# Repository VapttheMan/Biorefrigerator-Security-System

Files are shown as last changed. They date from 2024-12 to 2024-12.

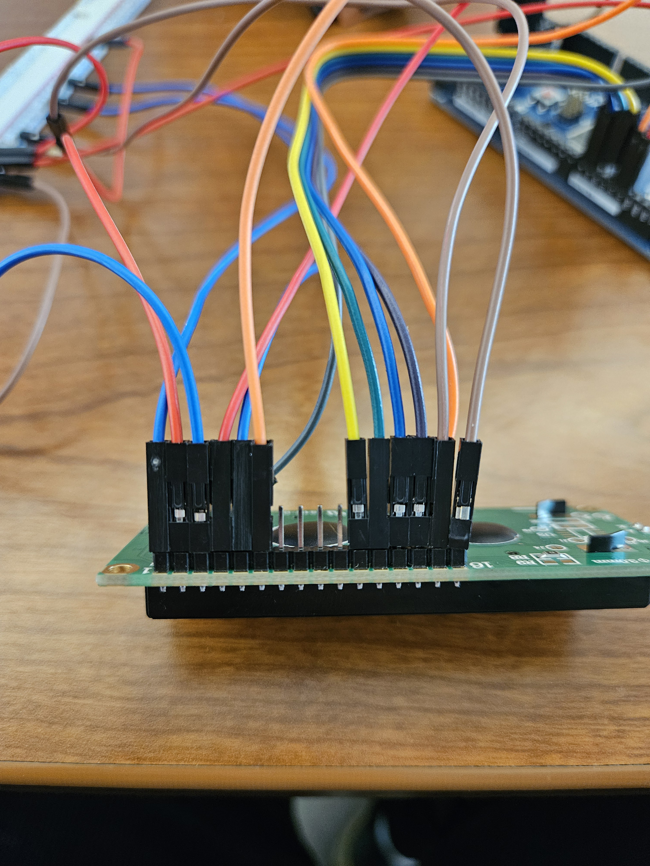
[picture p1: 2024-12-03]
1. Progress Reports/PR4/Photos/20240516_150257.jpg

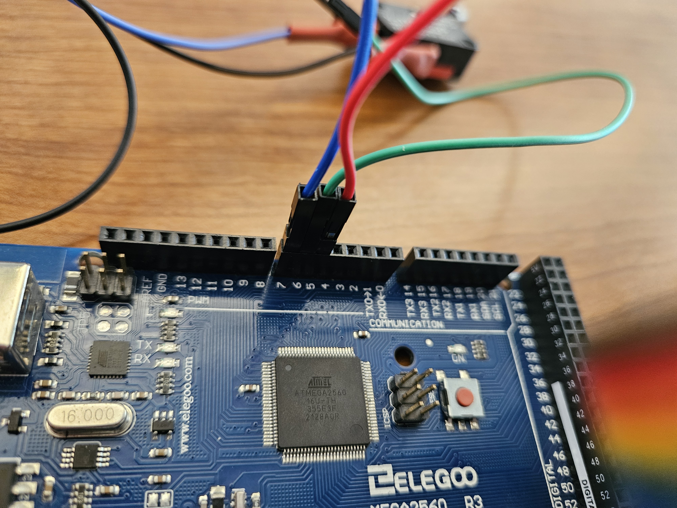
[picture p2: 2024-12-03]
1. Progress Reports/PR4/Photos/20240516_135011.jpg

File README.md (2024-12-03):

# Biorefrigerator Security System

**Contributors:**
- Brayden Chipman
- Vance Padilla
- Ashwin Halepet
- Miguel Cruz

**Note:** This project was initially uploaded to GitHub for visibility and sharing with potential employers and hiring professionals on platforms like LinkedIn. It was originally stored on Google Drive.

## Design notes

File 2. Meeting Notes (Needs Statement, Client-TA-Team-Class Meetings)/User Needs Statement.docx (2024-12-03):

Needs Statement:

Version 1:

A way to securely lock the fridges in lab settings to ensure people’s research samples are protected and consistently in the correct environment and something that is adaptable to multiple different types of refrigerators.

Directly from problem statement from client

Version 2:
There is a need for a lock for clinical refrigerators to prevent them from staying open due to the loss of samples

Version 3:

There is a need for a device to prevent clinical refrigerators from opening due to human error in order to prevent the loss of samples through thawing.

Too specific/Solution Oriented

Version 4:

There is a need to reduce the risk of contents in a controlled environment from being compromised due to unexpected/unwanted/unintentional access.

-Removes the focus on specifically refrigerators

Signs

Miguel Cruz (11/15/23, 7:55 PM)

Brayden Chipman (11/15/23, 7:55PM)

Vance Padilla (11/15/23, 7:55PM)

Ashwin Halepet (11/15/23, 7:55PM)

Version 5:

There is a need to reduce the risk of contents in a controlled environment from being compromised due to unexpected, unwanted, or unintentional access in frequently accessed refrigerators.

MC 11:13AM 11/28/23

BC 11:13AM 11/28/23

AH 11:14AM 11/28/23

VP: 11:14AM 11/28/23

Solution Statement:

There is a need to reduce the risk of contents in a controlled environment from being compromised due to unexpected, unwanted, or unintentional access in frequently accessed refrigerators by retrofitting features from more advanced and expensive products into older units. to prevent more major losses in costs.

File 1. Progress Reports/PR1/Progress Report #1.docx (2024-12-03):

Digital Lock for Clinical Refrigerators

Biomedical Engineering Senior Design

Dr. Aijun Wang

Progress Report 1

Fall 2023

Team 1

Miguel Cruz-11:08 am, 10/29/2023

Brayden Chipman-12:13 pm, 10/29/2023

Ashwin Halepet-12:38 pm, 10/30/2023

Vance Padilla - 3:38pm, 10/29/2023

Table of Contents

Problem Formulation 2

A. Background 2

B. Design Problem Statement 3

C. Objective 3

Needs Assessment 4

A. Survey Results 4

B. Needs Flow Chart 5

State-of-the Art 7

A. Introduction 7

B. Patent and Literature Search Results 7

C. Benchmarking Table 12

Preliminary Engineering Design Specifications and Constraints 15

A. EDS Table 15

B. House of Quality 16

References 18

Appendix 19

User Needs Survey R1 19

Additional Patents Chart 22

Client Interview 22

Meeting Minutes 24

Gantt Chart 25

# Problem Formulation

## A. Background

In preclinical and clinical laboratories, refrigerators and freezers are necessary tools for the preservation of samples such as biopsies, antibodies, and enzymes for use in testing and research. In certain situations, these samples can be irreplaceable. Unintentional thawing of these samples may render them unusable for the lab, leading to large losses in both time and money.

Refrigerators have gaskets, which are straps that are on the internal edge of the refrigerator door that seal the refrigerator shut. Inside a gasket is a magnet that uses attraction to shut itself to the metal of the refrigerator in order to seal shut [4]. Additionally, a refrigerator has hinges in order to close properly as well as open and close in a specific direction [6].

Refrigerators can fail to close for a variety of reasons, regardless of whether the refrigerator is in a laboratory environment or not. For instance, refrigerators could potentially lose the sealing capabilities of the gasket (the sealing that helps close the refrigerator door) due the gasket being dirty and old [5]. This can reduce the refrigerator’s capabilities of keeping shut. Another reason why the refrigerator might not be closing is because there are too many items inside the refrigerator and the items could prop the refrigerator door open in order to fit in. In environments where the internal temperature of the refrigerator or freezer is below freezing, ice buildup can also prevent the doors from properly closing. Furthermore, the refrigerator's magnets that can attract the metal of the refrigerator could potentially not function as well as usual, which results in the door potentially not closing properly [3]. Additionally, the refrigerator hinges can be damaged, which can prevent the refrigerator door from closing since the door cannot move properly if the hinges fail to operate properly [6]. Finally, another reason why a refrigerator door will not close is due to human negligence where a person did not shut it tightly enough or did not close it all the way [2].

To prevent this, many refrigerators have displays to show the internal temperature or alarms that go off when the temperature gets too low. Despite this, however, lab refrigerators still get left open often. A reason for this is likely because by time the displays show the low temperature, people are either gone or not paying attention and the samples are compromised. Additionally, alarms may not go off until after hours or may fail. If the equipment is old, it also may not have these features. If the refrigerators still work, a lock would be a cheaper and easier upgrade than installing alarms or displays.

Laboratories are environments in which the potential for human error can be very high. Laboratory refrigerators hold samples and materials that can potentially be worth hundreds of thousands of dollars in materials and research time. Based on client testimonials, laboratory refrigerators have been unintentionally left open, leading to large monetary losses.

## B. Design Problem Statement

Current locking systems for laboratory refrigerators and freezers fail to provide sufficient barriers to human error that would prevent the doors from being left ajar accidentally. Simple mechanical locks may ensure that the doors stay shut, but they lack network integration that would allow for users to verify that the door is shut properly or who has opened the refrigerator recently. The only current solution we have found that solves both issues is sold at a price that is not feasible for many labs, as most labs would have to buy multiple to ensure the integrity of their entire inventory[1]. This solution is the Beol Smart Lock as shown in the Benchmarking Table section. At $984 USD this lock is not feasible to order for the majority of labs. There are other digital locks on the open market that a consumer can buy. Such as on Amazon, where some locks can connect to personal devices and track worker’s usage of the locks (to better figure out who may have accidentally left the door open). However, none of these locks can be used on refrigerators without compromising the structure of the door. A digital refrigerator lock would have to exist solely on the exterior of the refrigerator system.

For these reasons, we aim to create an affordable digital device to increase security with refrigerated products by holding lab members accountable for ensuring the refrigerator door is shut.

## C. Objective

The objective of this senior design project is to develop a digital locking system for laboratory refrigerators and freezers that seamlessly interfaces with a dedicated digital application. We will provide a comprehensive solution that enhances the security and accountability of laboratory refrigerators. By addressing these major requirements and design inputs, the project aims to develop a digital locking system that is accessible, user-friendly, and cost-effective for a diverse range of laboratories.

Needs Assessment

## A. Survey Results

There is a disclaimer for the survey that was conducted by our team that responses from either us or the teaching assistant will be weighted as less than any other responses. Additionally, there are elements of the survey that we conducted that will be improved upon in future renditions of the survey in order to improve user feedback for the project’s user needs. We will make the survey more broadly to serve the needs of various customers since owning lab refrigerators is a very broad category of different users rather than needs based on only our client. We will base our survey more on the general needs of the users potentially impacted by digital locks in refrigerators rather than what aspects the customers desire for the end product. Furthermore, we plan on adding more text to the front of the survey in order to make it clearer on what the survey will accomplish.

The survey respondents of this survey vary from professors to teaching assistants to students. Besides ourselves and our teaching assistants, any other responder will be held in equal weight. However, due to some changes in how we will make our survey, any new responses will hold more weight than before since the new survey will be more polished and it will address problems with our survey. The current survey questions were planned to gauge user interest of needs and possible elements for the design; however, the new survey will go over more user needs. The questions that will be held in the most weight are the free response questions since a person can clarify and respond to their reasoning on why they weigh certain problems or needs more than others and it will help us gauge what is most important and what is the extent of the problems and needs users are facing. Our current survey based user needs off whether a user need is very important, useful but not important, and not important, which are defined as: very important means the user need is absolutely necessary for the design or else the design will not be as beneficial to users, useful but not important means the need is more nice to have but is not required, and not important means that the need is not essential to the final design.

Based on the survey results, the majority of the users do not have any form of locks or securing mechanism to secure their lab refrigerators. A slight majority of users have had their refrigerators open at least once throughout their time in a laboratory environment. Some users indicate a lack of worry with their refrigerators as they have not had issues with refrigerators opening. However, other users have had problems with their refrigerator security either through older parts of the refrigerator or due to unreliable alarm and lock systems. The survey responders universally indicated that they desire a lower priced product in order to save money as well as a smaller product anywhere up to a maximum size of a foot.

## B. Needs Flow Chart

The most important requirement is to safeguard the integrity of valuable laboratory samples. The digital lock system will provide a remote locking and unlocking mechanism for refrigerator doors, directly addressing the critical user need to prevent unintentional spoilage of samples due to doors being left ajar. A primary design input is the creation of a system capable of reliably protecting these valuable, often irreplaceable, samples.

Another core consideration is the prioritization of personnel accountability. This requirement calls for the integration of digital features that enable real-time user logs and remote alerts. By tracking and recording personnel interactions with the locking mechanism, the project aims to enhance accountability within laboratory settings. The design input focuses on creating a digital application that seamlessly syncs with the locking system, facilitating user management and monitoring.

Additionally, cost-effectiveness is a key aspect of the objective. The project aims to design an affordable solution that overcomes the high price barriers associated with existing locking systems. This design input aligns with the overarching need for an economical digital device that improves security and accountability, ensuring accessibility for laboratories of varying sizes. Cost-effectiveness also ties into another direct need from end users, that being the longevity of the product. It is a major benefit to end users to have a product that will not have to be replaced for some time.

In addition to these major requirements, there are other considerations that, while not primary requirements, would be valuable inputs for the design of the locking device. A user-centric approach is something to consider, with the aim of creating a user-friendly interface that simplifies the process of remote locking and unlocking. In the process of making this product more accessible, interacting with the locking system becomes easier. This however, is not a characteristic that would drastically impact the functionality of the product. This approach addresses the need for an intuitive digital application and locking mechanism design, making it easy for laboratory staff to use.

Compatibility and integration are also considerations for the design. The digital lock system should seamlessly fit a wide range of refrigerator models commonly found in laboratories, addressing the diversity of laboratory equipment. The design inputs will focus on ensuring compatibility and integration capabilities.

Security was one of the characteristics that was not a priority for many, given the survey results. Given that the primary clientele of this product is laboratory staff, there was not as much a concern of stealing, rather a concern that the refrigerator doors stay closed. As a result, physical barriers towards theft and physical damage were not of a higher priority.

Below is shown the needs flow charts which summarizes what considerations are essential to not needed.

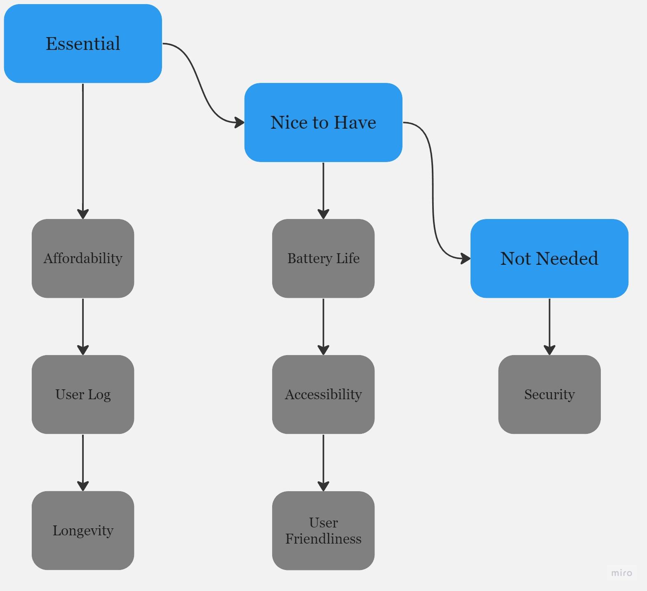
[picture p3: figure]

# State-of-the Art

## A. Introduction

While there have been some similar refrigerator lock products on prior patents, including some with digital unlocking and locking systems, none have had digital locks that connect internet enabled devices. Aside from that, these devices have features that we could draw inspiration from for our digitized refrigerator locks, as well as information on what features are missing from the current market.

## B. Patent and Literature Search Results

I. US20210071940A Patent

i. Cooler and Freezer Lock

ii.William Denison, Calin Roatis

iii. The product is a lock that can be utilized to open and close a freezer. Access is controlled with controllers that can unlock and lock the refrigerator door. There is a digital component to these locks as each controller is controlled by a microcomputer. Furthermore, there is an electronic system in the device in order to help perform the unlocking and locking actions. A drawback of this system is that the lock is a complicated design that can confuse users. This product can serve as inspiration for our potential device since the digital lock will be an electronic system and we can base our product on this in order to gain inspiration on how to create an electronic designed digital lock.

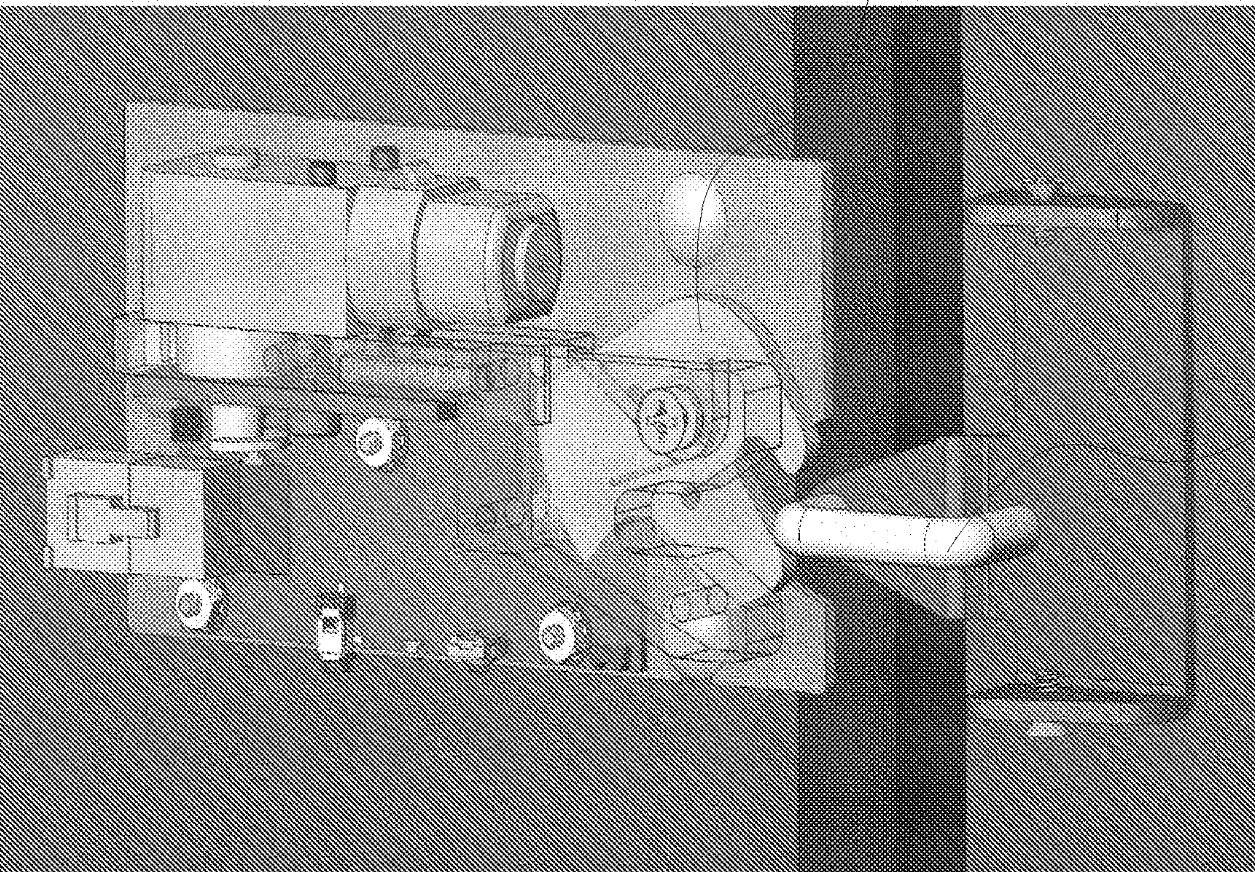
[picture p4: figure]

II. US7768378B2 Patent

i. Field retrofittable refrigerator lock with audit trail

ii. Brian R. Hill, Steven A. Belzek, Robert Brewcyznski, Kenneth A. Kaczmarz, Mitchell S. Mlynarczyk, Francis H. Zimmerman, Ernest Vaughn

iii. The product is a refrigerator lock with a number punch-in code attached on the front of the lock in order to secure the refrigerator with a passcode. The product contains digital components due to the punch in code that resembles a phone. The product can track user information, as well as when the user opened and closed the refrigerator. The main drawback of this product is that the phone system that is used is rather dated and most people use more digital versions of phones in this day and age. However, this product can serve as inspiration since this product uses a phone network, similarly to how a digital lock has a phone like interface within a digital app, in order to ensure the lock is locked.

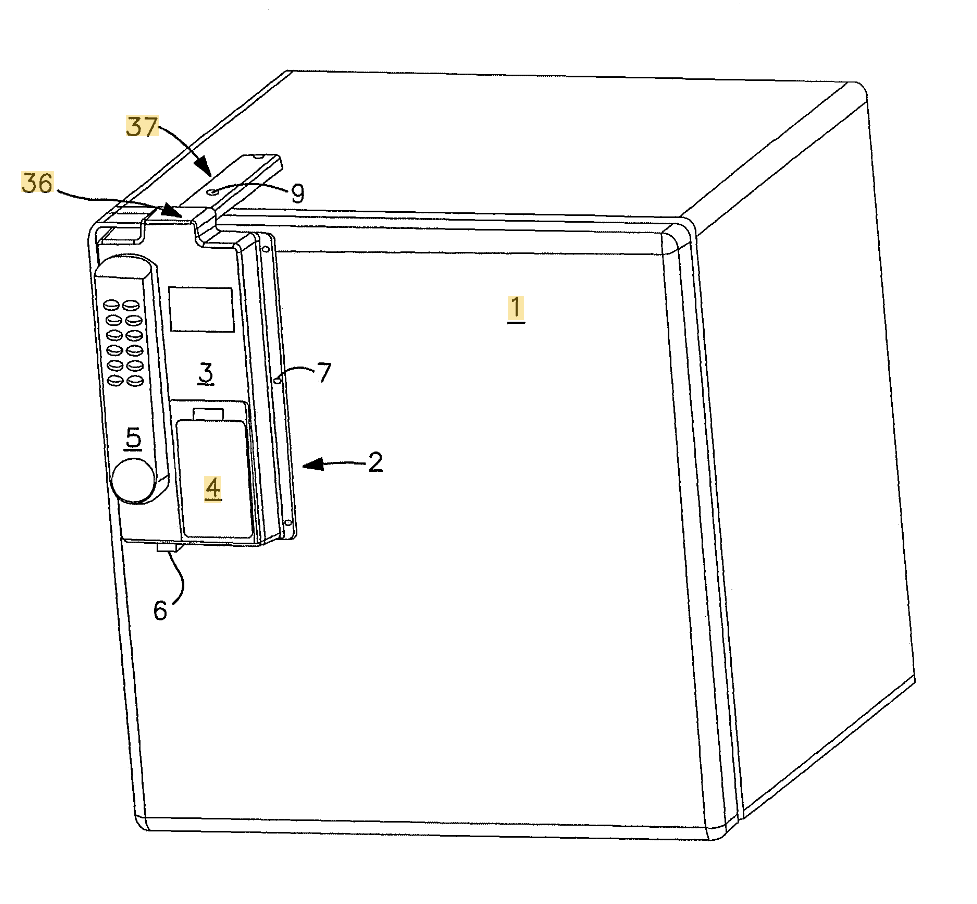
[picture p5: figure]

III. US8063735B2 Patent

i. Remotely actuated refrigerator lock with thermal spoilage protection

ii. Norman A. Shoenfeld

iii. The product is a remote door lock system that can be accessed via a computer. The product can be connected to a computer either by ethernet or by a USB system. The product can track the temperature and humidity within the system so that when the temperature and humidity reaches a threshold, the remote connected unlocking and locking will be disabled in order to regulate temperature and humidity. This product also maintains a log of people who access the refrigerator. The biggest drawback of this design is that it is a rather large device that does take up space. This design is relevant to our brainstorming process since this design is remotely controlled and that it connects to devices via some form of an external network.

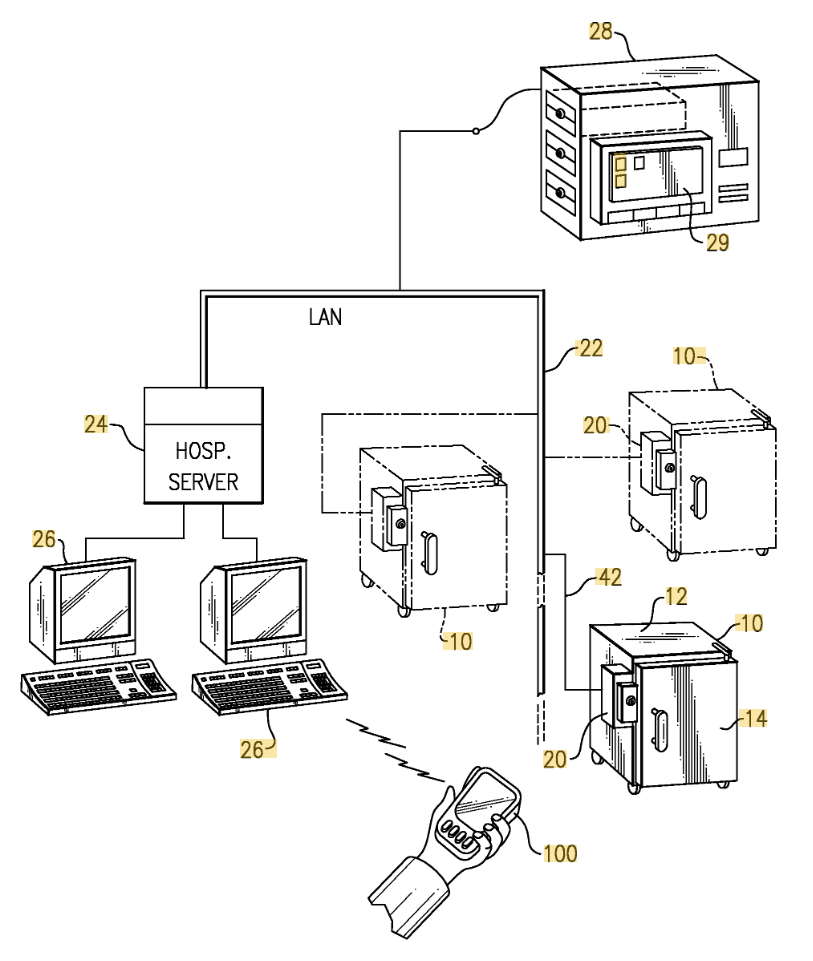
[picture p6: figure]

IV. US20170219271 Patent

i. Refrigerator Locking System

ii. Carl Kent Abrahamson

iii. This product is a lock that can lock multiple doors of the refrigerator at once in just one location of the refrigerator. This is a quite versatile lock since it can close a number of locks at once in the same refrigerator cabinet while not requiring any additional devices or parts. A drawback of this device is that there is not anything digital about this device. This could serve as inspiration for if we decide to expand the product and create a device that can close multiple refrigerator doors at once.

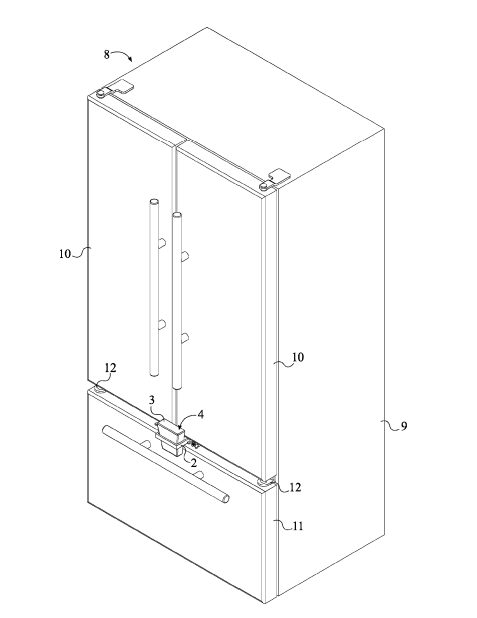
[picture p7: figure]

V. Becton Dickinson Pyxis ES Refrigerator

This device is a refrigerator that stores medications and encodes in the users so that the doctor knows who uses what medicine that is stored in the refrigerator as well as the location. This device requires signing in and signing out in a screen that is on the refrigerator in order to access the medication, hence why this device is a digital lock. Furthermore, this device has a physical key spot so that a person could also access it with a physical key. There are various versions and sizes of this device depending on user needs. A drawback of this device is that the screen has a lot of options and it can get complicated when looking for the basic items since the screen keeps a vast log of medications and users, though it is only a light drawback. This device can serve as inspiration for our future device since it can give us ideas on how a sign in feature can work on our app as well as some ideas on aspects of the app to add.

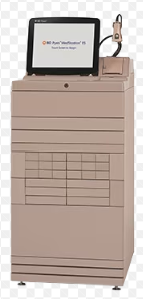
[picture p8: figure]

There have been previous recalls on digital refrigerator unlocking and locking devices used for storing biological and/or medical substances, though they are limited in frequency. There have been prior problems where a user signs in to access the refrigerator and the refrigerator does not open. According to MAUDE, in 2021 and 2022, there has been one recorded incident in both years for the Becton Dickinson Pyxis ES Refrigerator, where the refrigerator refused to unlock due to a malfunction, and as a result, a customer could not get their medications that the doctor prescribes, even though in one of the cases, the patient refused treatments. This is a very serious recall since if a patient needed to get their needed medicine, if the refrigerator refuses to unlock, then the patient could ultimately die since they could not get their medicine. Our digital lock should automatically open when a user chooses the unlock option as well as have a physical override.

## C. Benchmarking Table

Due to the specificity of the problem that this project is meant to address, a benchmarking table was created in order to compare the important metrics of similar products. The benchmarking table is a neat and convenient method to collect ideas on what one can expect in terms of price and other metrics based on similar devices. The user needs that were chosen were based on survey results as well as team discussions with each other, the Teaching Assistant, and the client. The benchmarking table compares similar products’ solutions to user needs along with their metrics and units. The BEOL Biological Refrigerator Smart Lock was chosen to be benchmarked and compared due to the fact that it is the only current digital locking solution for refrigerators in a laboratory setting that is on the market, even though they only sell in China and the pricing is high. Due to the high feature set and price of the BEOL lock, this lock can be considered very useful yet very niche. The goal of this project is to make a more widely accessible lock while still maintaining much of the specialized functionality that comes with network and remote integration. The reason the Sifely Smart Lock was chosen is because the product is a digital lock used for any lock that connects to a phone app. While not direct competition for the product this project seeks to create, the Sifely Smart Lock sets a general guideline for features and a user interface that users are satisfied with in regards to remote control of the lock and with everyday usage. The YEYA Refrigerator Lock was chosen based on the information that it was one of the best selling refrigerator locks on Amazon, a shopping service that would be widely available to people both in and out of labs. By using this device as one of the products to benchmark, one is able to compare current user needs to a general refrigerator lock without any digital capabilities, similar to a control group in an experiment.

BENCHMARKING TABLE 10-20-23

TEAM 1: Brayden Chipman, Miguel Cruz, Ashwin Halepet, Vance Padilla
Need | Metric | Units | BEOL Biological Refrigerator Smart Lock * | Sifely Smart Lock | YEYA Refrigerator Lock
1 | Cost | US Dollars | $984 | $129.99 | $13.99
2,4,6,7 | Remote Connectivity | Binary | Yes | Yes | No
4,7 | Size | Centimeters | 15.9 cm x 8.8 cm x 3.6 cm | 17.78 cm x 7.62 cm x 2.84 cm | 25.4 cm x 6.60 cm x 2.54 cm
3,7 | Material | Type | PC-ABS engineering plastics | Zinc | Polypropylene Plastic
3,7 | Strength | Young's Modulus of Material(MPa) | 1670-11100 MPa | 96500 MPa | 800-8250 MPa
3,4,6,7 | Method of Attachment | Type | Adhesive | Installation on Door | Adhesive
4,5,7 | Power Delivery | Type | 2 AA Batteries | 4 AA Batteries | N/A
2,6,7 | Method of Verification | Type | NFC Card, physical key, remote authorization | App, Fingerprint, Passcode | Key
7 | Alarms/Notifications | Binary | Yes | Yes | No
4,6 | Weight | Kilogram | ~3 kg | ~1.65 kg | 0.2 kg
4,6 | Used Outside of Labs | Binary | No | Yes | Yes
1 | Affordability | *Translated using DeepL Translation
2 | Records
3 | Longevity
4 | User Friendly
5 | Battery Life
6 | Accessibility
7 | Security

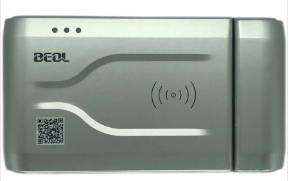
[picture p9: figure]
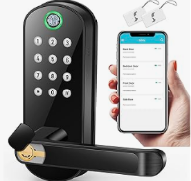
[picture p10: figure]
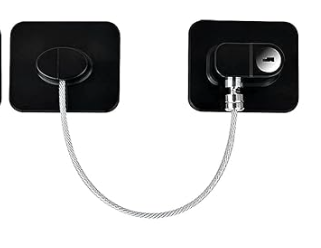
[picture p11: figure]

Images
Description of Products | | | This is a digital lock that was specifically designed for biological refrigerators. It includes a temperature monitor, and features that can close the lock based on changes in temperature. | This is a digital lock that has unlock and lock features connected to a mobile application used to replace the traditional lock and doorknob system. | This is a non-digital lock that is held by a thick wire. The black squares are held up by adhesives that stick to the refrigerator.

# Preliminary Engineering Design Specifications and Constraints

## A. Target Values

This is the current rendition of the preliminary engineering design specifications table. Each of the design metrics was created with one central user need in mind. However, due to the overlapping nature of the needs and properties required to satisfy those needs, most metrics have interplay with each other. One example of this would be the metrics relating to the attachment of the device, as the method of attachment is also directly related to the strength of that attachment.

Given the feedback from the user needs survey, the metrics that were of high importance to the product’s design were size, price, remote connectivity, notifications, method of attachment, strength of attachment, strength of material, user log, and weight. The size and weight of the device were determined through an average of the competition. The device should be small and light enough to be easily installable, yet not to the point where the device loses physical strength. Therefore, by averaging the values of known products that successfully accomplish their task, the product has a starting point in terms of size and weight. Price was a major concern for a large portion of the survey respondents, and the maximum price was determined to be 300 USD. The closest device to the product that this project is meant to create is the BEOL Biological Refrigerator Smart Lock, which is sold at nearly 1000 USD. Obtaining similar functionality at around 300 USD would make this product much more attractive towards consumers with multiple refrigerators that need to be secured. The user log, notifications, and remote connectivity are all metrics that were decided to be nearly essential to the functionality of this project, and were only present on the expensive BEOL lock. By allowing for users to have access to these more modern features, this product is meant to bridge the gap between the very expensive, feature rich locks and the standard physical locks that are commonly used in older or less funded labs.

Metrics | Units | Corresponding User Needs | Range | Target Value | Direction of Improvement
Size | Centimeters | User Friendliness | 2cm-30.48cm | 16.0 cm x 8.0 cm x 4.0 cm | To be minimized to a point
Price | US Dollar | Affordability | $14-$984 | $~300 | To be minimized
Remote Connectivity | Binary | User Friendliness | N/A | Yes | N/A
Notifications | Binary | Accessibility | N/A | Yes | N/A
Method of Attachment | Type | Longevity | Adhesive or Installation | Acrylic Based Adhesive | N/A
Strength of Attachment | N | Durability | 100-200 | 135 | N/A
Strength of Material | GPa | Durability | 0.8 to 96.5 | 69 (6061 Aluminum) | To be maximized
User Log | Binary | Records | N/A | Yes | N/A
Weight | kg | User Friendliness | 1 kg to 4 kg | 2 kg | To be minimized

## B. House of Quality

After creating a benchmarking table to help compare important metrics of similar products and creating an engineering design specifications table (EDS), combining both tables together will create a house of quality. Not only does the house of quality provide many of the details from both the benchmarking table and the EDS table, the house of quality helps us understand the technical aspects within the customers requests and how each metric focused on affects other metrics required for this device. The house of quality also provides relative weight prioritization and customer importance that is judged based on survey responses. Benchmarking and EDS data is mostly displayed on the bottom.

The house of quality helps greatly with correlating between needs and functional requirements. The table shows that the needs of affordability, user friendliness, and security have many strong relationships with the functional requirements. The house of quality also shows that remote connectivity, and material heavily affect the needs that customers want. The table also displays correlations between each functional requirement. Cost and strength of attachment have many correlations to consider when developing the product. Material, cost, and method of attachment will greatly affect the strength of attachment positively while the use of this product outside of labs may correlate with a decrease in cost. Based on the needs shown on the survey, users request many functional requirements to be improved which are all shown on the house of quality. Remote connectivity, power delivery, method of verification, alarms/notifications, and use outside of labs want to be greatly improved while cost of the product wants to be greatly decreased.

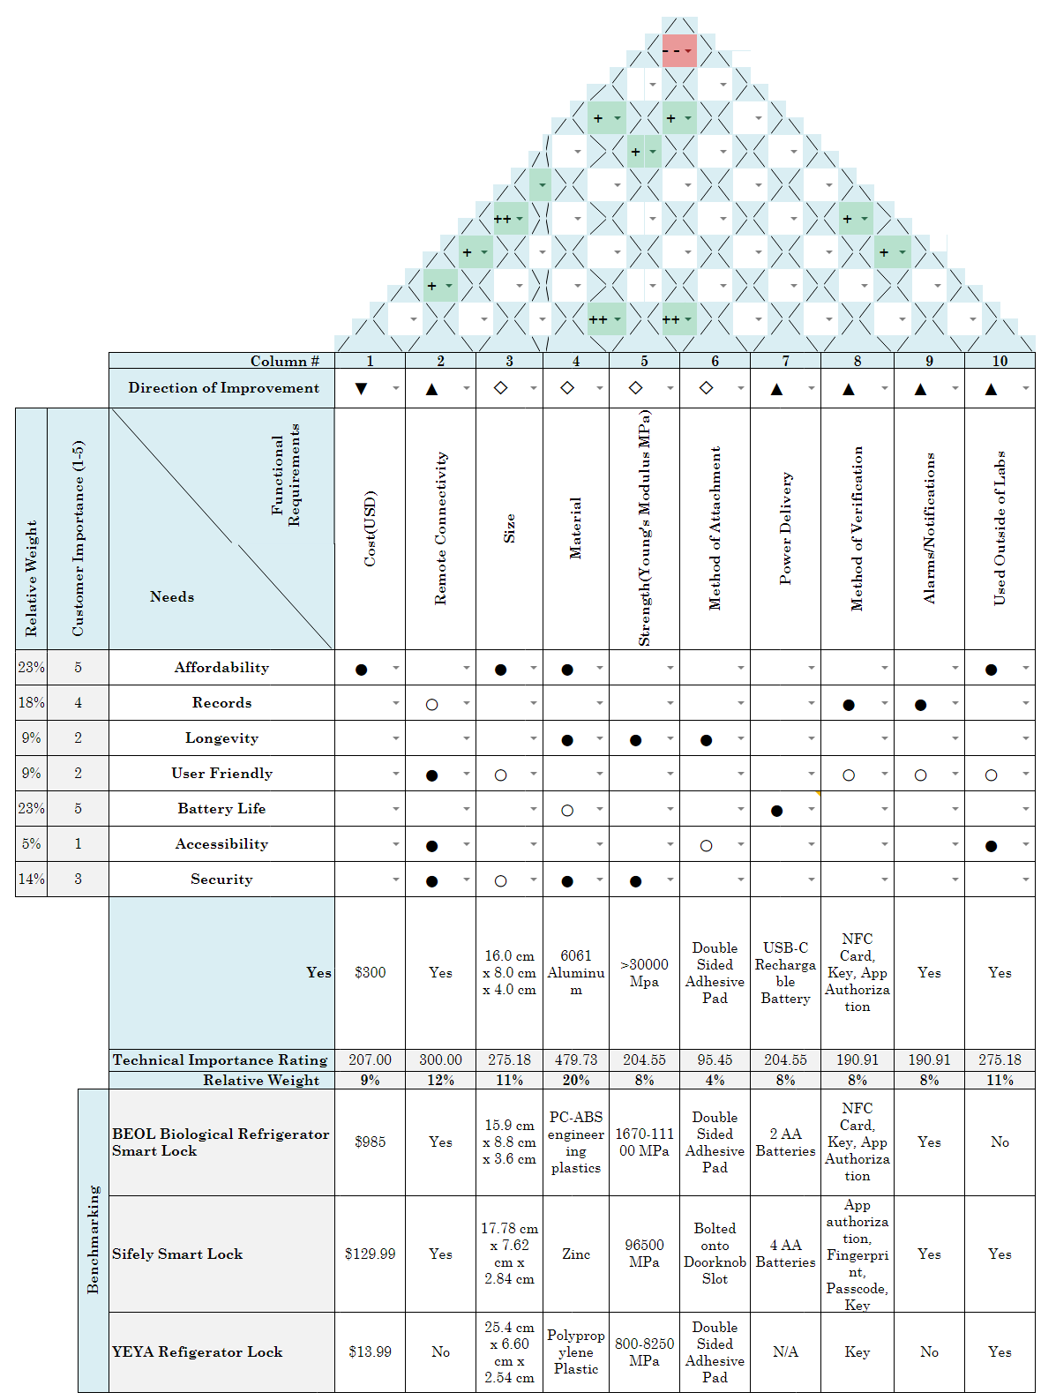
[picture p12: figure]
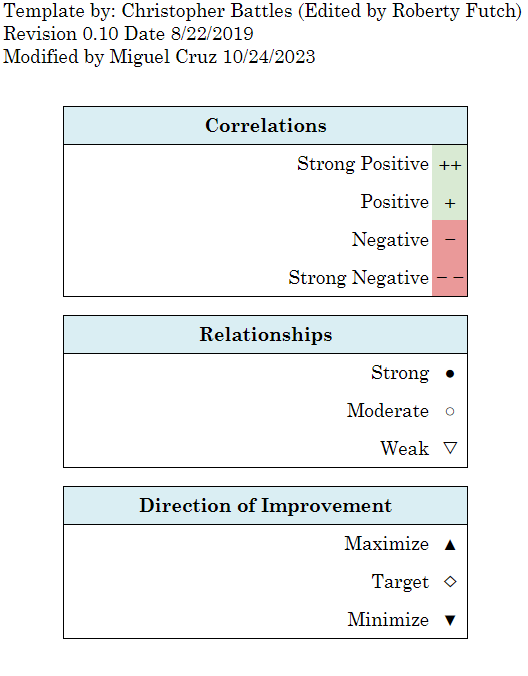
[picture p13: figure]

# References

1. “BEOL贝尔科技生物冰箱智能锁 报警智能冰箱锁 电子锁.” 百度爱采购 - 国内优质的批发采购平台、货源批发网、进货渠道, Qingdao Bell Intelligent Technology Co., Ltd., Accessed 28 Oct. 2023.
2. Appliance, Advanced. “The Fridge Door Won’t Close Properly: Reasons & Solutions.” Advanced Appliance Repair Service, 27 Feb. 2023, Accessed 28 Oct. 2023.
3. “10 Ways to Repair a Refrigerator Door That Won’t Close.” Flamingo Appliance Service, 16 July 2019, Accessed 28 Oct. 2023.
4. Blumberg, Perri Ormont. “Why You Should Clean Your Refrigerator Door Gaskets ASAP.” Southern Living, Dotdash Meredith, 3 Feb. 2020, Accessed 28 Oct. 2023.
5. Crabb, George. “How to Remagnetise a Fridge Door Seal - FIRST4MAGNETS: Blog.” FIRST4MAGNETS, 30 Mar. 2023, Accessed 28 Oct. 2023.
6. Rheuby, Dev. “Selecting the Best Refrigerator Door Hinges: What You Need to Know.” HingeOutlet, HingeOutlet, 6 June 2023, Accessed 28 Oct. 2023.
7. “Maude Adverse Event Report: CAREFUSION 303 Pyxis Es Refrigerator; Automated Dispensing Cabinet.” Accessdata.Fda.Gov, FDA, Accessed 28 Oct. 2023.
8. “Maude Adverse Event Report: Marion Veterans Affairs Medical Pyxis ES Refrigerator; Automated Dispensing Cabinet.” Accessdata.Fda.Gov, FDA, Accessed 28 Oct. 2023.
9. “Overview of Materials for Polypropylene, Molded.” MatWeb, Accessed 28 Oct. 2023.
10. Denison, William, and Calin Roatis. “US20210071940A1 - Cooler and Freezer Lock.” Google Patents, Google, 11 Mar. 2021, Accessed 28 Oct. 2023.
11. Hill, Brian R., et al. “US7768378B2 - Field Retrofittable Refrigerator Lock with Audit Trail.” Google Patents, Google, 3 Aug. 2010, Accessed 28 Oct. 2023.
12. Shoenfeld, Norman A. “US8063735B2 - Remotely Actuated Refrigerator Lock with Thermal Spoilage Protection.” Google Patents, Google, 22 Nov. 2011, Accessed 28 Oct. 2023.
13. Abrahamson, Carl Kent. “Refrigerator Locking System .” Free Patents Online, Anaqua, Inc., 3 Aug. 2017, Accessed 28 Oct. 2023.
14. “Pyxis Medstation ES System .” 50136, Becton Dickinson, June 2013, Accessed 28 Oct. 2023. 50136.com.au/wp-content/uploads/2016/03/Pyxis-Medstation-ES-Station-User-Guide.pdf.

# Appendix

## User Needs Survey R1

Our group utilized Google Forms in order to conduct a survey of various questions. We conducted the survey in order to gain insights on what are the most important user needs to keep in mind during the project. Additionally, we used the survey to understand the extent of the problems with lab refrigerators being left open. Below are the questions that were used in the survey.

Part 1: Introductory Questions

Our group will be conducting a senior design project on creating a digital lock system in order to ensure that refrigerators in the lab are secured. Occasionally in labs, the refrigerator accidentally gets left open, and the consequences can be devastating since open refrigerators can compromise hundreds of thousands of dollars in research. To help prevent this, our group will create a lock that is connected to an app so the lock can secure the refrigerator from being left ajar or slipping open, as well as being able to limit access to selected personnel.

The main information that will be needed for this project are the current issues with locking systems for lab refrigerators and ways that users wish to use the device digitally. We also need other information about possible features that, while not necessary, may be wanted by enough people.

This survey is designed to gather information about needs and wants important to potential end users of our product.

What is your name and email?

Does your lab use locks or any securing mechanism to make sure the refrigerators stay closed?

- Yes
- No

If you answered yes to the previous question, answer the following questions:

Please describe your current system of securing your refrigerator.

What are some issues you have experienced with your current system?

Part 2: User Needs For The Digital Lock

This section is for figuring out the priorities of the end users based on the current locking solutions.

How often have the lab freezers/refrigerators accidentally stayed open throughout your time in the lab?

- 1-2 times
- 3-4 times
- 5 or more times
- Never

Based on your current refrigerator lock solutions, please list the top three design elements that were insufficient in your experience.

Please explain why these features are insufficient.

Please explain your experience with security around your lab.

Part 3: Future Design Elements

This section is about your priorities in looking at possible future design elements for a digital refrigerator lock. Please state your level of priority by selecting one of the three following options: Very Important, Useful But Not Important, and Not Important.

How important is it to be able to monitor the temperature of the refrigerator and have it notify you?

- Very Important
- Useful But Not Important
- Not Important

How important is it to have an app that is associated with the digital lock to record usage of the refrigerator or turn on/off the lock on the refrigerator?

- Very Important
- Useful But Not Important
- Not Important

How important is it that the lock be very difficult to break into?

- Very Important
- Useful But Not Important
- Not Important

How important is the ability for the digital lock to open or close refrigerator doors remotely?

- Very Important
- Useful But Not Important
- Not Important

Based on the previous questions, explain why what you chose is of high priority.

If you would like to explain other priorities that have not been listed, please explain here. Please provide your experience on why this is a priority.

Part 4: Design Input Target Values

When constructing this lock, what are some restrictions that might need to be considered during the design process?

What is the highest price range you would be willing to pay for this product?

- $0-$150
- $150-$300
- $300-$450
- Greater than $450

What are the maximum dimensions for the lock system (full height, width, and depth)?

Are there any other specific details and restraints that one should consider when constructing this refrigerator lock?

Part 5: Free Response

Please give any final statements that you believe must be considered when creating a refrigerator lock. All concerns or ideas will be considered for this project.

Write down any other questions, concerns, or any other essential ideas that have not been listed that you have about this digital lock app project.

## Additional Patents Chart

Patent Number | Title | Inventor | Current Assignee | Source
US20210071940A | Cooler and Freezer Lock | William Denison, Calin Roatis | Individual | https://patents.google.com/patent/US20210071940A1/en?oq=US20210071940A
US7768378B2 | Field Retrofittable Refrigerator Lock with Audit Trail | Brian R. Hill, Steven A. Belzek, Robert Brewczynski, Kenneth A. Kaczmarz, Mitchell S. Mlynarczyk, Francis H. Zimmerman, Ernest Vaughn | CompX International Inc | https://patents.google.com/patent/US7768378B2/en?oq=US7768378B2US7768378B2
US8063735B2 | Remotely Actuated Refrigerator Lock with Thermal Spoilage Protection | Norman A. Shoenfeld | S&S X Ray Products Inc, SIS X Ray Products Inc | https://patents.google.com/patent/US8063735B2/en?oq=US8063735B2
US20170219271 | Refrigerator Locking System | Carl Kent Abrahamson | Individual | https://patents.google.com/patent/US20170219271A1/en?oq=US20170219271

## Client Interview

We met with our client twice. The first meeting was utilized to understand the scope of the project. We discussed the user needs of our client, we learned more on what the current problem is with refrigerator security, which was that refrigerators get left open either on their own or by accident and that can result in loss of years of research and money. We explored the laboratory our client worked in to gain a sense of the environment our client works in. We asked some clarifying questions on potential user needs and priorities. Additionally, we gained some input on survey questions to ask on our surveys. In our second visit, we looked at the Sifely Smart Door Lock to gain some inspiration on potential ideas on what our potential device could look like and also explore how smart locks work.

## Meeting Minutes

Task | 10/8-10/14 | 10/15-10/21 | 10/22-10/28 | 10/29-11/4
Team Meeting | 2 hour | 1 hr | 1 Hr
Client Meeting | 1 Hour | 1 hour
Weekly Deliverables | User Needs Survey | Benchmarking Table | EDS
Miguel Cruz | 50 min | 1.5 hr | 1 hr
Brayden Chipman | 1 Hr 20 min | 1 Hr | 1 hr
Vance Padilla | 1 Hr | 1 Hr | 1 hr
Ashwin Halepet | 1 Hr
Research
Miguel Cruz
Brayden Chipman
Vance Padilla
Ashwin Halepet
TA Meeting | 1.5 hr | 30 min | 1 hr
Project Progress Report
Miguel Cruz | | 2 hr | 3.5 hr
Brayden Chipman | | 2 hr | 4 hr
Vance Padilla | | 1.5 hr | 3 hr
Ashwin Halepet | | 1.5 hr | 2.5 hr

## Gantt Chart

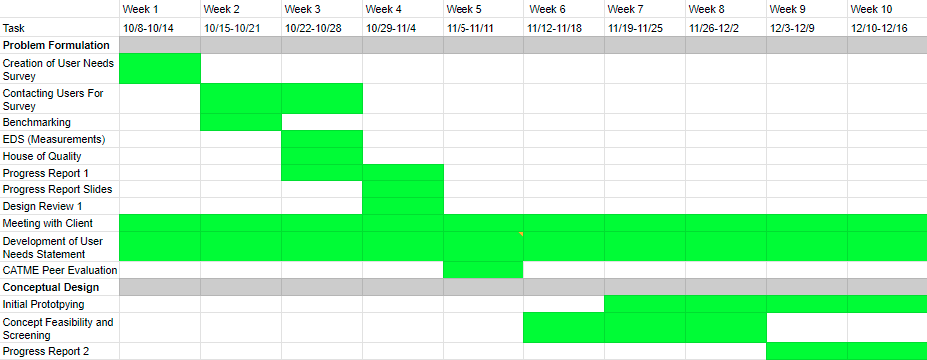
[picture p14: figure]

Page is here just so the next page is vertical

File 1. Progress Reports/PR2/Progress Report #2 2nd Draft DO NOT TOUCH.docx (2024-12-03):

Biorefrigerator Security System

Biomedical Engineering Senior Design

Dr. Aijun Wang

Progress Report 2

Winter 2024

Team 1

Brayden Chipman

Miguel Cruz

Ashwin Halepet

Vance Padilla

Table of Contents

Problem and Objective 2

Problem 2

Objective 2

Concept Generation 3

Concept Generation Flow Chart 3

Primary Design Concepts 3

Concept Screening 8

Primary Screening 8

Secondary Screening 10

Materials and Manufacturability 12

Detail Drawings 15

Concept 1 15

Concept 2 16

Concept 3, Final Concept Chosen, Initial Design 16

References 19

Appendix 20

# Problem and Objective

Figure 1: Introductory Figure for the Design

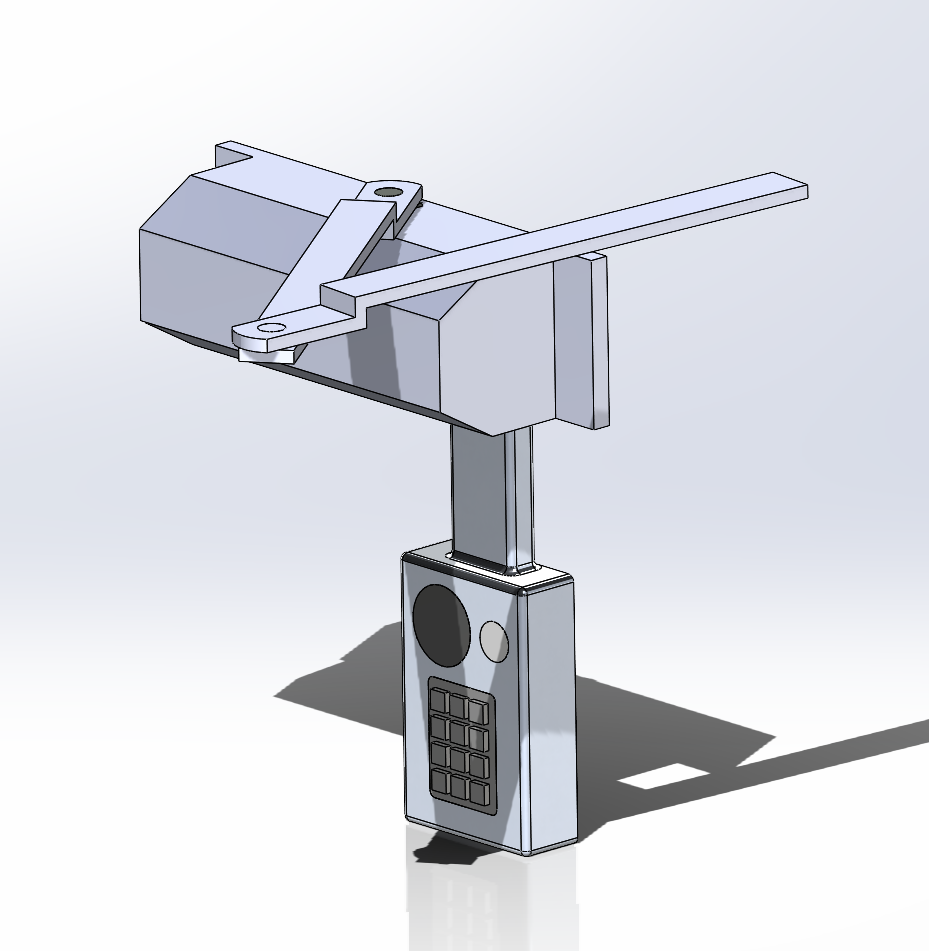
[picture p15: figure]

Above is the current prototype design for the lock sensor system. The device is a weighted system that can ensure that the door is closed but has a light and sound sensor system as a failsafe in case the door is left open.The progress report will go into more details on this design in the Detail Drawings section.

## Problem

Current methods of ensuring that frequently accessed controlled laboratory environments (CLEs) remain closed are limited by the need for human input, which requires a human to physically close the CLE. Humans typically interact with the CLE by opening or closing the doors manually. Requiring the use of human input introduces the possibility of human error. However, there is no concrete way on how a CLE can signal that it is accidentally left open or not closed all the way. The most common error of human input in CLEs is accidentally leaving them open. This error can result in significant risk to the integrity of materials within them, such as DNA or cells.

## Objective

The objective of the Biorefrigerator Security System is to implement a device that minimizes the risk of sample deterioration due to prolonged exposure to ambient conditions. We aim for the device to be power efficient, affordable, easy to install, and easy to use. By both controlling and reporting the status of CLE doors, our device can be used by laboratory staff to autonomously close the doors. Primary intended use cases are CLEs such as chemical and biological laboratory refrigerators.

Concept Generation

## Concept Generation Flow Chart

When designing a CLE door security device, we primarily were considering two key factors: sensors and digital or analogue components. Emphasizing simplicity was a primary concern in order to minimize human error and robustness against system failure. Our initial ideas only involved using the door, so therefore we decided to consider a hinge mechanism. We realized that considering the most ideal components in the design would help us decide what and how to design the device. By combining components and ideas that cover for each other’s weaknesses, we could create a product that efficiently satisfies our defined criteria.

Figure 2: Mind Map

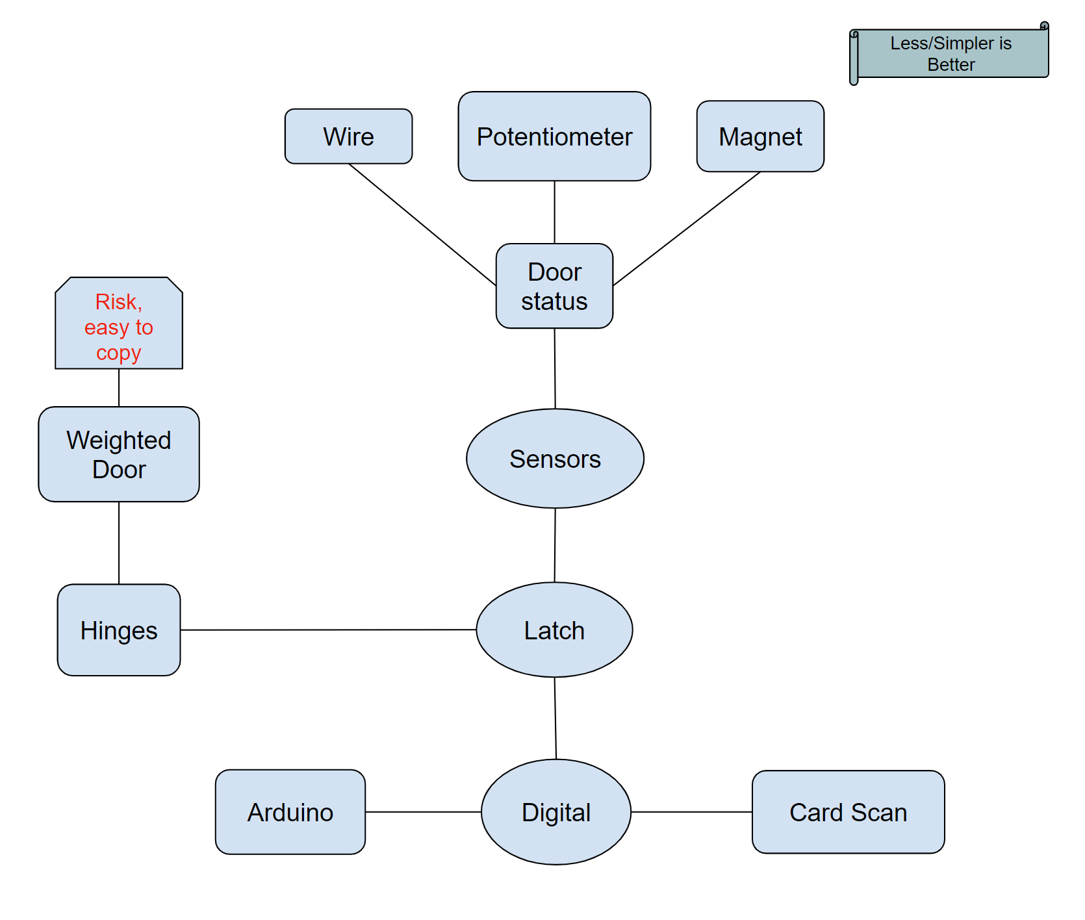
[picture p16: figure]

## Primary Design Concepts

When we looked back at our concept generation flow chart, we realized that our prototype will be based on multiple different concepts that are integrated together. Our primary screening for our prototype is based on three components: detection, security, and alarm. Specific components we will screen are discussed below and will have a description of why each component was considered.

Concept Component Section 1: Input(Detection/Status)

All components listed below contribute to the detection or remote signaling of door status.

Laser (Opto Slotted Switch)

An infrared laser sensor will detect the open or closed status of the door. An LED attached to the door side of the design will shine a light onto a phototransistor, which will cause it to conduct when the CLE door is closed. The conductance of the phototransistor will determine the closed state.If the CLE door is open, then the laser will move with the door and the phototransistor would not conduct [1]. This component was chosen due to the simple nature of the design, as well as the passive nature of applying it. In addition, infrared sensors that function similarly are commonly used in households, making it a very established technology.

Magnetic

A simple coiled magnetic sensor consists of three main components: a magnet, a coil, and a device to measure current or voltage. By attaching the magnet to the door of the CLE and the coil to the main body, the opening and closing of the door will act as the movement for the magnet. When the magnet and coil are separated more, the coil will decrease the induced current applied to the coil, which then can be interpreted as the doors being open [2]. Utilizing the motion of the door moving away from the body of the CLE would make the implementation of a coiled magnetic sensor simpler.

Temperature

A temperature sensor, or thermocouple, will be placed on the inside of the CLE. A thermocouple works by measuring the net open current voltage at the cold junction between two dissimilar metal wires. This net open circuit voltage is a function of temperature and composition of the two wires. Temperature and voltage are then correlated in order to report temperature [3]. The temperature is kept at a certain temperature inside the CLE, and when open, the temperature increases as ambient heat transfers into the CLE. If the temperature increases past a user specified point, then the sensor will detect that the CLE has been left open for too long. This technology is also well established, and temperature is one of the main factors that must be controlled in order to preserve materials in CLEs.

Weighted

An automatic weighted door will actively close the CLE if the door is left open. The weighted closing system is based on existing automatic door closers, which is a mechanical hydraulic device. Springs are used to exert force onto the door to close it when it is open, while the hydraulic components are used to control the speed of closing by moving closer to or further away from the spring [4]. This component was chosen because of the ability to change the status of the door as opposed to monitoring it. It was also a robust system for automatic door closing that minimized user interaction so as to not impede the work of laboratory workers.

Wire

A wire will be set between the CLE’s door and main compartment. The wire, or cable, will be held in a retractable cord reel. Retractable cord reels utilize a torsion spring mechanism to build tension when the cable is pulled. After the door is let go, the potential energy in the torsion spring is released and used to retract the cable[5]. Hooke’s law is used to calculate the amount of force that is exerted on the door during retraction. This method was considered due to the existence of retractable cable reels in the market, as well as the ability to autonomously close the CLE door.

Rotary Potentiometer

A rotary potentiometer can be placed at the hinge of the door and can detect the door’s status. Potentiometers work by utilizing the fact that an object’s resistance is directly proportional to its length. A rotary potentiometer works by moving a sliding contact across a uniform resistive strip. Changing the length of the path that current flows through effectively changes the effective resistance [6]. The angle that the potentiometer is at when the door is closed will determine the reference resistance. From this, a reference voltage can be calculated and the sensor can be calibrated. Changes in the resistance from the reference will correlate to an increase in output voltage due to the voltage divider circuit [7]. The linearity of rotary potentiometers also means that the degree that the door is opened to can be easily calibrated to output voltages.

Concept Component Section 2: Input(Security/Verification)

All of the following components below are based on security factors to check who opens the door.

Pin Pad

Using a pin pad can allow people who only know the passcode enter or have everyone have their own passcodes to know who specifically opens the CLE door. A pin pad system is a type of number code system where when a code for the CLE door is entered, the CLE system will be opened or closed. The reason why this idea was considered is because using a pin pad is another intuitive way to unlock a CLE and disarm an alarm since all it takes to use a pin pad is to type in a short code and that is it.

Finger Pad (Optical Fingerprint Sensor)

A optical fingerprint sensor can be used to access the door while knowing who specifically opened the door. The sensor itself uses LEDS to create a scan of one’s fingerprint using a charged-coupled device(CCD). A CCD uses an array of pixels that respond to light hitting the sensor in order to generate an image that captures the ridges and valleys of a person’s fingerprint[9]. By comparing a scanned fingerprint to those registered by the operator in a database, the microcontroller is able to determine if the user is authorized or not. The reason why this idea is considered is because this method ensures that only authorized users can access the CLE, while making it easy to add new users to that pool. In addition, the scanner does not require the user to carry any extra authentication with them, such as a key or card.

Card Reader

Most labs in UC Davis have an RFID card for each person who works in a lab. RFID cards work by using low power radio frequencies to collect and store data. A transceiver reads and then transmits radio frequencies to the cards. The cards themselves will be RFID tags that contain small computer chips that can transmit data to the RFID reader. We can use a card with the CLE lock to tell who is opening the door since the preexisting security systems of the building include a tracking system that can be used to identify the user of the card through transmissions from the card’s chip[8]. The card reader will be a way to verify a person authorized to use the contents of the CLE is opening the door instead of someone else, especially since some lab areas (such as our client’s) have multiple groups using the same space [8]. This idea was considered since using card readers comes naturally for many people as IDs and credit cards are commonly used in people’s daily lives so ID usage is very user intuitive. Furthermore, using an idea to unlock CLE’s is simple since all it takes is placing a card near the scanner to verify.

Concept Component Section 3: Alarm/Notification

All of the following components are supposed to alert the user by notification or alarm. Having no alarm is also an option as well.

Digital

A digital notification would send an alert to the phone or computer of the administrator of the lab from an application. This solution necessitates either an internet connection in order to use Firebase Cloud Messaging (FCM) or another system to send notifications and dictate when to send them [12]. For this device, we will send a notification whenever our detection system finds the door to the CLE open. The signal of the circuit will be triggered when the door is in a position that is not the usual closed position and will send a notification to notify a user that the CLE is open.

Sound Alarm

A sound alarm on the device can alert those in the area by creating an audible noise that a CLE had been left open and that the samples inside are prone to denaturing or being compromised. A sound alarm can also create a sense of urgency or annoyance that will compel a user to close the CLE in order to stop the alarm. The sound alarm will be connected to the circuit board. What will trigger the sound alarm to activate is if there’s any movement within the sensor outside of what it senses as a closed position of the CLE, the signals will be sent from the sensor to the sound alarm and then the sound alarm will activate an audible noise.

Light Alarm

A light alarm on the device can provide an easy visual alert for a user to see that the CLE has not been shut all the way in order for the user to prevent the samples from degrading due to the CLE being open for too long. Additionally, a strobing light can act as a silent alarm to alert users who may be hard of hearing or deaf. Similarly to a sound alarm, the light alarm is connected to the circuit board, and it is triggered if the sensor attached to the refrigerator door senses some form of difference in the position from a closed door position, which will send an oscillating voltage to the alarm to make the LED strobe[13].

No Alarm

Having no notification system could be feasible with solutions that guarantee the door closing when left open. Furthermore, it requires no extra materials. This solution comes with the downside that, should the closing device malfunction, no one would know without manually checking.

# Concept Screening

## Primary Screening

- Table 1: Primary Screening of Input Method Concepts

Input(Status/Verification) | Concept Variants
| | Laser/Optical | | Magnetic | | Temperature
Selection Criteria | Weight | Rating | Weighted Score | Rating | Weighted Score | Rating | Weighted Score
Power Delivery | 10% | 3 | 0.3 | 3 | 0.3 | 4 | 0.4
Affordability | 10% | 4 | 0.4 | 4 | 0.4 | 3 | 0.3
Longevity | 5% | 3 | 0.15 | 5 | 0.25 | 3 | 0.15
Ease of Use/User Friendliness | 25% | 5 | 1.25 | 4 | 1 | 5 | 1.25
Ease of Handling/Accessibility | 10% | 4 | 0.4 | 3 | 0.3 | 5 | 0.5
Ease of Manufacturing | 20% | 4 | 0.8 | 3 | 0.6 | 3 | 0.6
Practicality (Is it Ideal/Proven to work?) | 15% | 5 | 0.75 | 2 | 0.3 | 5 | 0.75
Security | 5% | 2 | 0.1 | 2 | 0.1 | 1 | 0.05
Score | | 4.15 | | 3.25 | | 4
Notes
| | Weighted | | Wire | | Rotary Potentiometer
Selection Criteria | Weight | Rating | Weighted Score | Rating | Weighted Score | Rating | Weighted Score
Power Delivery | 10% | 5 | 0.5 | 5 | 0.5 | 4 | 0.4
Affordability | 10% | 3 | 0.3 | 5 | 0.5 | 4 | 0.4
Longevity | 5% | 4 | 0.2 | 5 | 0.25 | 4 | 0.2
Ease of Use/User Friendliness | 25% | 5 | 1.25 | 4 | 1 | 5 | 1.25
Ease of Handling/Accessibility | 10% | 5 | 0.5 | 3 | 0.3 | 5 | 0.5
Ease of Manufacturing | 20% | 4 | 0.8 | 4 | 0.8 | 4 | 0.8
Practicality (Is it Ideal/Proven to work?) | 15% | 5 | 0.75 | 5 | 0.75 | 3 | 0.45
Security | 5% | 1 | 0.05 | 4 | 0.2 | 1 | 0.05
Score | | 4.35 | | 4.3 | | 4.05
Notes | | Doesn't need alarms | | possible entanglement, Highly rated but not preferred
| | PinPad | | FingerPad | | Card
Selection Criteria | Weight | Rating | Weighted Score | Rating | Weighted Score | Rating | Weighted Score
Power Delivery | 10% | 3 | 0.3 | 3 | 0.3 | 3 | 0.3
Affordability | 10% | 3 | 0.3 | 2 | 0.2 | 2 | 0.2
Longevity | 5% | 5 | 0.25 | 2 | 0.1 | 3 | 0.15
Ease of Use/User Friendliness | 25% | 5 | 1.25 | 3 | 0.75 | 3 | 0.75
Ease of Handling/Accessibility | 10% | 4 | 0.4 | 3 | 0.3 | 4 | 0.4
Ease of Manufacturing | 20% | 4 | 0.8 | 2 | 0.4 | 3 | 0.6
Practicality (Is it Ideal/Proven to work?) | 15% | 5 | 0.75 | 5 | 0.75 | 5 | 0.75
Security | 5% | 5 | 0.25 | 5 | 0.25 | 4 | 0.2
Score | | 4.3 | | 3.05 | | 3.35
Notes

Table 2: Primary Screening of Notification Method Concepts

Notifications | Concept Variants
| | Digital | | Sound Alarm | | Light Flashing | | No Alarm
Selection Criteria | Weight | Rating | Weighted Score | Rating | Weighted Score | Rating | Weighted Score | Rating | Weighted Score
Power Delivery | 10% | 2 | 0.2 | 3 | 0.3 | 3 | 0.3 | 5 | 0.5
Affordability | 10% | 2 | 0.2 | 4 | 0.4 | 4 | 0.4 | 5 | 0.5
Longevity | 5% | 2 | 0.1 | 3 | 0.15 | 3 | 0.15 | 5 | 0.25
Ease of Use/User Friendliness | 25% | 3 | 0.75 | 4 | 1 | 4 | 1 | 1 | 0.25
Ease of Handling/Accessibility | 10% | 4 | 0.4 | 5 | 0.5 | 5 | 0.5 | 1 | 0.1
Ease of Manufacturing | 20% | 3 | 0.6 | 5 | 1 | 5 | 1 | 5 | 1
Practicality (Is it Ideal/Proven to work?) | 15% | 4 | 0.6 | 5 | 0.75 | 4 | 0.6 | 1 | 0.15
Security | 5% | 5 | 0.25 | 3 | 0.15 | 2 | 0.1 | 1 | 0.05
Score | | 3.1 | | 4.25 | | 4.05 | | 2.8
Notes | | Possibly use as secondary aspect

Looking at the primary screening, we rated each component based on the following criteria: power delivery, affordability, longevity, ease of use/user friendliness, ease of handling/accessibility, ease of manufacturing, practicality, and security. Each of these comes from an updated version of the User Needs Flowchart. To clarify the differences between ease of use and ease of handling, ease of use is a customer's ability to quickly understand how to use the product while ease of handling is a customer’s ability to physically interact with the product. Practicality is to determine whether previously devices using the component were used well or well received. Security, while initially thought to be highly prioritized, has significantly less weight as security has been proven to be high through other means. Overall, the ease of use and ease of manufacturing was set to have the highest weight. We want the customer to be able to quickly understand our product and we want to have easy manufacturing in order to have quick prototyping and quick reiterations of the device.

We divided all components into different colors categories: red, yellow, and green. The red category means that the component is poorly rated. After checking and talking with the team, the red components were not considered to move on to the secondary screening. The yellow categories could have been well-rated overall, but they will not move on to the secondary screening after proper deliberations between team members. For example, the wire system was highly rated, but it still seemed very intruding and obstructive to people wanting to open the door no matter where we placed it since a wire system would end up being tough to untangle and maneuver, and therefore, was moved to the yellow category. Finally, the green components were selected based on their high rating as well as being well received between team members and therefore, moved onto the secondary screening. Green-rated systems indicate that they are not too difficult to manufacture, take up a reasonable amount of space, and include user-friendly methods for interacting with the system. Note that we did not blindly select random green components for our secondary screening, but rather deliberated over which components would work best in the green category. Overall, we made 3 concept ideas to be put for the secondary screening.

## Secondary Screening

Table 3: Secondary Screening Table

Concepts | Concept Variants
| | Concept 1 (Laser Sensor) | | Concept 2 (Rotary Potentiometer + PinPad) | | Concept 3 (Weight + PinPad)
Selection Criteria | Weight | Rating | Weighted Score | Rating | Weighted Score | Rating | Weighted Score
Power Delivery | 10% | 3 | 0.3 | 3 | 0.3 | 4 | 0.4
Affordability | 10% | 4 | 0.4 | 3 | 0.3 | 4 | 0.4
Longevity | 5% | 3 | 0.15 | 4 | 0.2 | 4 | 0.2
Ease of Use/User Friendliness | 25% | 5 | 1.25 | 4 | 1 | 5 | 1.25
Ease of Handling/Accessibility | 10% | 4 | 0.4 | 4 | 0.4 | 4 | 0.4
Ease of Manufacturing | 20% | 4 | 0.8 | 4 | 0.8 | 4 | 0.8
Practicality (Is it Ideal/Proven to work?) | 15% | 5 | 0.75 | 4 | 0.6 | 5 | 0.75
Security | 5% | 2 | 0.1 | 5 | 0.25 | 4 | 0.2
Score | | 4.15 | | 3.85 | | 4.4
Rank | | 2 | | 3 | | 1

For our secondary screening, we created 3 concepts. We will go over these concepts in more detail in our detailed drawings sections where example designs are shown. To put simply, the first concept involved just the laser component, the second with the rotary potentiometer and pin pad, and third with the weighted door and pin pad. All three concepts all include sound and light alarms. These concepts will be our initial prototypes for our devices and we will reiterate and change as we go. Selection criteria remained the same and the highest score of the three will not automatically be chosen as the prototype to work on, but rather deliberated over then chosen. The initial concept drawings will be in the Detail Drawings section later on in the progress report.

Result: Concept 2 was the best choice decided from our team. We took into account the scoring of the other concepts and deliberated rather than just accepting the highest score and going with that concept. Having the concept 3 prototype (weighted door and pin pad) seems best as it actively closes the door meaning considering the door being left open is less likely. The alarms provided in the concept will be emergency alarms just in case the weighted door fails.

Overall, we realized that instead of checking the status of the door, we can instead work on changing the status of the door when it is in an open state.

# Materials and Manufacturability

A couple of issues that arose from the initial design were the material choice, implementation of the rotary potentiometer, wiring, and methods of attachment. After meeting with Steven Lucero from the TEAM Lab, a few modifications were made to the initial design concept that we had created. In terms of the external design itself, not much was changed aside from the expansion of the surface that would connect to the top of the CLE. The manufacturing process of the finalized design will include the machining of aluminum for the body. Interior parts that do not experience significant stress will be 3D printed.

For the pin pad, we decided on a body that is made of 6061 aluminum as it is manufacturable and durable for the purposes of this project. We will have a microcontroller system in order to be able to get the code into the alarms, pin pad, and potentiometer system. A red and green LED light system will be installed on the outside of the device to signal the alarm status of the CLE door. We will have screws to attach various parts of the device. Permanent epoxy resin will be used in order to secure the final device to the CLE. PVC copper coating wires will be used as the wiring for the electronic components of the device, and these wires will be given enough length to allow for the movement of the arms. The closer will be modified in order to utilize the hydraulic components in the device for the closing action. The speaker will be placed inside the main housing body to act as an auditory alarm. A potentiometer will be used to measure the angle of the door to detect whether the door is open or not in the event that there is an obstruction.

The closer will be milled at 600 rpm in order to create a channel for the cables to run through[14]. The sheets of aluminum will be laser cut and welded to create the box shape, then chamfered down for refinement.

## Bill of Materials

Table 4: Bill of Materials

Component | Material | Purchasing Location | Part Number | Quantity | Weight | Price Per Unit | Total Price | Notes | Link
6061 Aluminum | 6061 Aluminum | Amazon | N/A | 2 | 1.755 lbs per sheet | $18.99 | $37.98 | The body for the pin pad | 6061 Aluminum Component Link (https://www.amazon.com/Aluminium-Aluminum-Finely-Polished-Deburred/dp/B08M63VD66?hvadid=507685853899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)
Screws | 18-8 Stainless Steel | McMaster-Carr | 97613A529 | 1 | ~0 | $17.36 | $17.36 | For the Body attachment. 10 Pack | Screws (https://www.mcmaster.com/97613A529/)
Adafruit METRO | Microcontroller | Adafruit | 2488 | 1 | 0.042 lbs | $17.50 | $17.50 | Coding component for alarms, pin pad, potentiometer | Adafruit (https://www.adafruit.com/product/2488) METRO (https://www.adafruit.com/product/2488)
Red and Green Indicator LED | LED | Adafruit | 4042 | 1 | Not Available | $1.75 | 1.75$ | Light Alarm | RED/GREEN LED Link (https://www.adafruit.com/product/4042)
Pin Pad | N/A | Adafruit | 3845 | 1 | ~0 | $6.50 | $6.50 | The pin pad itself | Pin Pad Link (https://www.adafruit.com/product/3845)
Wires | PVC Coated Copper | Amazon | B08BBXTBL7 | 1 | 0.79 lbs total | $14.94 | $14.94 | Wiring for the device | Wires (https://www.amazon.com/Gauge-Wire-Solid-Core-Hookup/dp/B08BBXTBL7?s=hi)
Potentiometer | Potentiometer | Adafruit | 562 | 1 | Not Available | $0.95 | $0.95 | 10k kiloohms | Potentiometer (https://www.adafruit.com/product/562)
Adhesive (Epoxy) | Epoxy Resin | Amazon | N/A | 1 | 0.125 lbs total | $12.45 | $12.45 | 2 pack, Metal Adhesive | Epoxy Resin (https://www.amazon.com/J-B-Weld-Original-Reinforced-Strength/dp/B0B5VNG2YT?hvadid=598238944920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)
Speaker | N/A | Adafruit | 1891 | 1 | 0.01 lbs | $1.75 | $1.75 | Speaker for the alarm | Speaker (https://www.adafruit.com/product/1891)
Closer | Aluminum | Amazon | ‎SOULONGg850ya231w | 1 | 2.31 lbs | $20.81 | $20.81 | Will use for hydraulic components | Closer Link (https://www.amazon.com/Aluminum-Commercial-Automatic-Closing-Independent/dp/B08GPD3W6V?hvadid=680463214693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)
Internal Brackets and other small parts | PLA | UC Davis | N/A | As needed | ~0 | Variable | Variable
Resistor | 10kΩ 5% | Adafruit | 2784 | 1 pack | ~0 | $0.75 | $0.75 | For voltage divider | 10kΩ resistor (https://www.adafruit.com/product/2784)
Battery Holder | | Adafruit | 67 | 1 | 0.05lbs | $3.95 | $3.95 | | https://www.adafruit.com/product/67
Servo | Micro Servo | Adafruit | 2307 | 1 | 0.03lbs | $11.95 | $11.95 | | Servo (https://www.adafruit.com/product/2307)
Battery | 9V battery | Amazon | N/A | 1 pack of 4 | 0.05lbs | $9.55 | $9.55 | Power source for device | 9V battery (https://www.amazon.com/Amazon-Basics-Performance-All-Purpose-Batteries/dp/B0774D64LT?th=1)
Sum of Prices/Weights | | | | | ~7 lbs | | $158.19

## Purchasing

The components from the Bill of Materials will be purchased from their respective vendors, however some may also be sourced from preexisting stock at UC Davis in order to save time in shipping. The Bill of Materials is based on the current idea for the final design, and may be revised later on due to needs that have not arisen at this time.

## Rapid Prototyping

3D printing will be used for rapid prototyping of the design. PLA will be used in order to print the arms and main body of the case for prototyping purposes in order to minimize time and budget spent on machining. The dollar amount spent on 3D printing will vary depending on the amount of times revisions may need to be done, and thus this will be calculated and added to the finalized version of the Bill of Materials once prototyping has concluded.

# Detailed Drawings

## Concept 1

Our first concept is a laser detector door opening device with a sound and light alarm, addressing the need to reduce the risk of contents in frequently accessed CLEs from being compromised due to unexpected or prolonged access. The device employs a laser sensor, laser padding, and a light and sound box powered by AA batteries. By detecting the presence or absence of laser reflections off the phototransistors, the sensor determines whether the door is open. In the event of an open door, the device activates a light and sound alarm, alerting nearby individuals to the situation, and automatically deactivates when the door is closed. Despite concerns about security and longevity, the solution's quick and simple development, along with its ease of use, compensates for these drawbacks. The device's passive nature ensures minimal user interference, making it suitable for environments where active security measures may be impractical. Technical feasibility involves addressing precision challenges, exploring similar laser sensors, and identifying potential stimuli that could interfere, with an estimated prototype development and testing time of approximately four days. The solution's non-obvious and novel aspects include its passive operation and integration of alarm systems and laser sensors into a single physical unit, making it applicable in areas with limited network connectivity.

Figure 3: Different Views of Concept 1

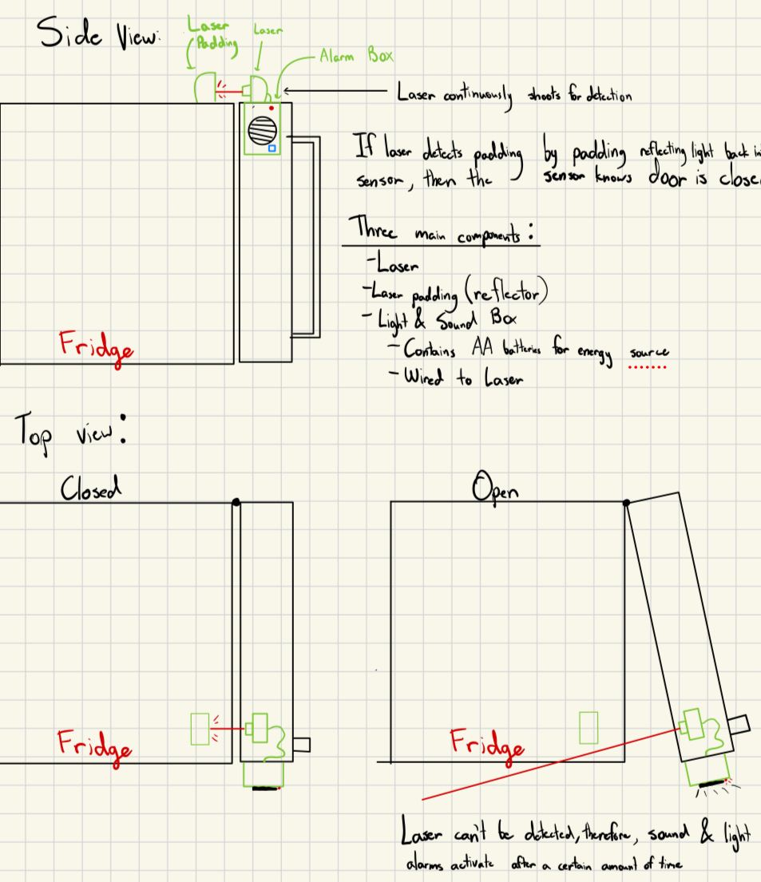
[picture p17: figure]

## Concept 2

The following concept involves the integration of a rotary potentiometer at the hinge of a CLE door, coupled with a PinPad and alarm system to address the need for enhanced security in frequently accessed CLEs. The PinPad allows users to input a code, disarming the alarms triggered by the rotary potentiometer, which monitors the door's open and closed status through a potentiometer. If the door remains open beyond a specified time, the alarms activate with sound and flashing lights. The key components include a motherboard, PinPad with LED, potentiometer, and a speaker box with AA batteries. This design utilizes the potentiometer to modulate electrical resistance, translating it into different voltage readings corresponding to the door's angle. Pros include non-obtrusive installation at the hinge and providing a precise, nuanced measurement of door openness. However, concerns revolve around affordability, potential variations in CLE hinge designs, and power consumption. Technical feasibility is largely favorable, but questions about handling and power requirements need addressing. The concept's novelty lies in using a potentiometer for CLE security, offering a more nuanced approach than existing binary systems.

Figure 4: Different Views of Concept 2

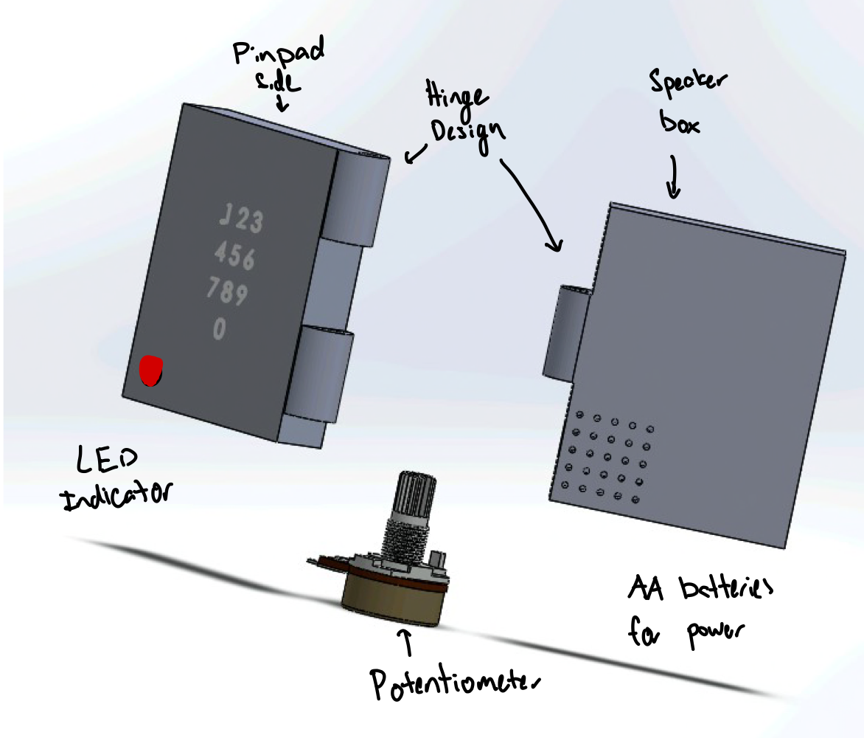
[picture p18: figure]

## Concept 3, Final Concept Chosen, Initial Design

The final and chosen concept to start working for prototyping addresses the need for enhanced security and automatic door closure in frequently accessed CLEs. The design incorporates a weighted mechanism, utilizing a spring and sensor, to ensure reliable closure of the CLE door. A pin pad lock provides a secure means of access, allowing users to input a passcode for unlocking and locking the door. Additionally, a sound and light alarm system activates if the CLE is opened without the pin pad, requiring manual closure and passcode entry to disarm the alarm. The weighted mechanism serves a dual purpose, automatically closing the door after a specified time and acting as a failsafe in case of alarm-triggered failures. Despite potential concerns regarding ease of manufacturing, this concept excels in providing heightened security, ease of use, and practicality, addressing the critical need to prevent unauthorized access to the CLE's contents while not completely having to worry about the door being left open. These factors set it apart from previous prototypes, offering a unique and effective solution to enhance the overall security of frequently accessed CLEs.

Figure 5: First Design for Concept 3

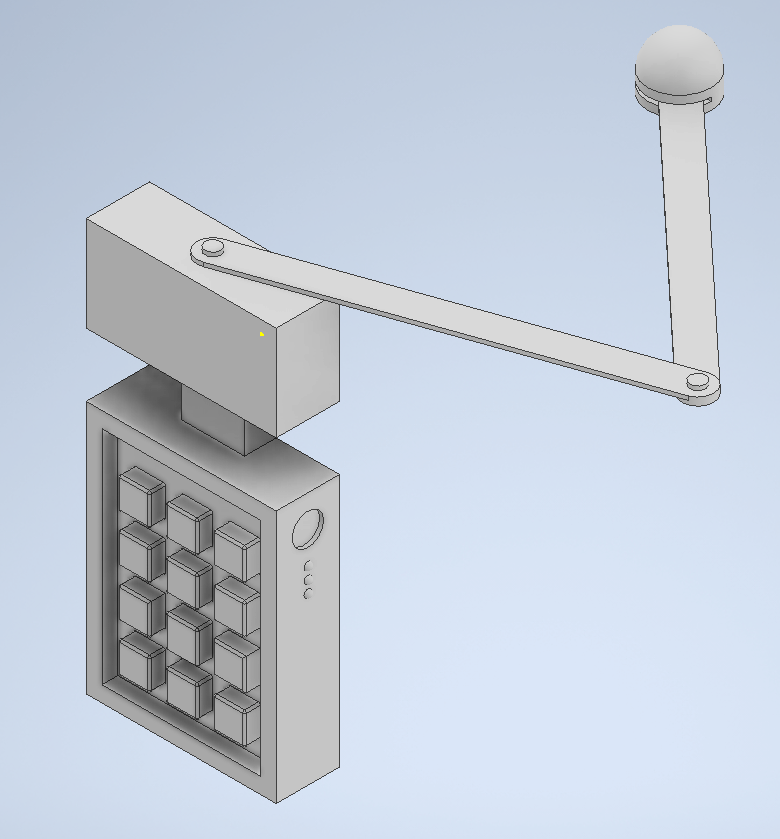
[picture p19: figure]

Figure 6: Version 2 of Concept 3, taking projected parts into account and using Solidworks. Made of 6061 Aluminum.

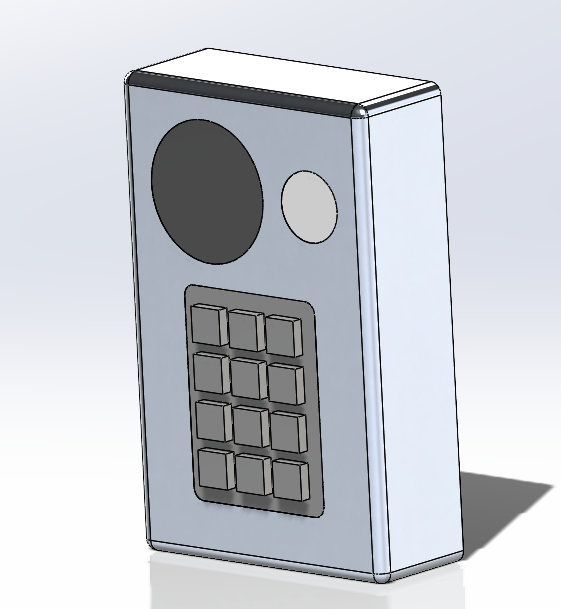
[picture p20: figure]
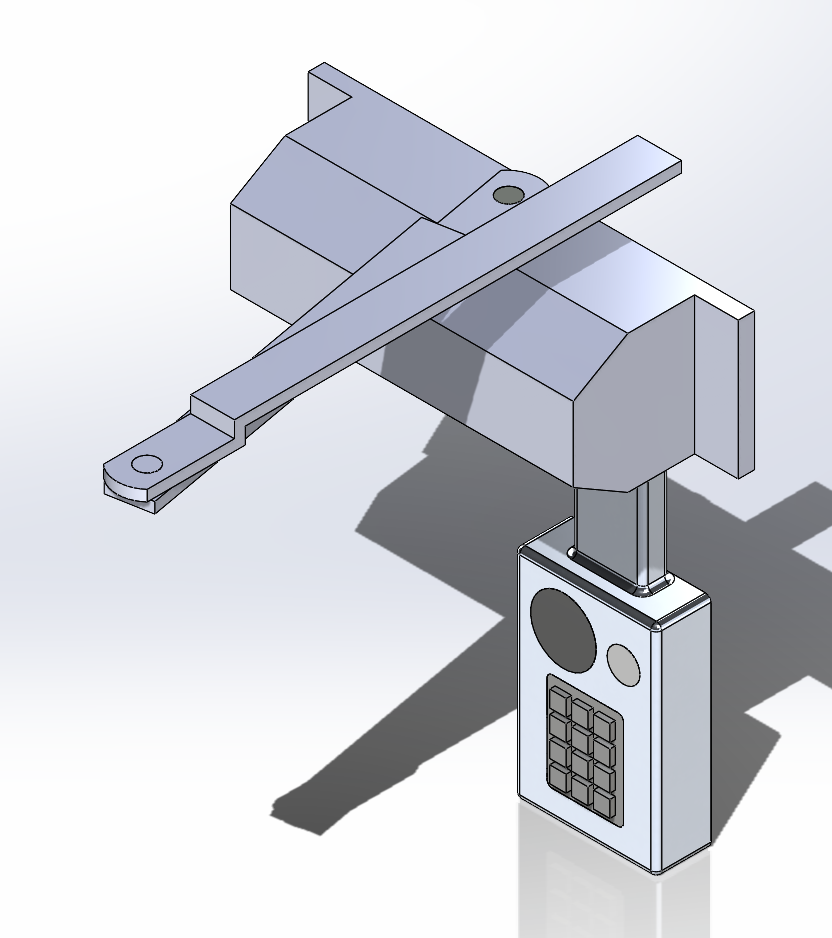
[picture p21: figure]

The newly proposed design involved a more visible and clearer location to add our sound and light alarm shown above the pin pad. Since we also have a purchased pin pad that we will use, the design shows where the pin pad will be placed. Inside will have our Arduino to communicate and function between the pin pad, sound alarm, and light alarm, and finally our rotary potentiometer. The hydraulic weighted mechanism is now properly displayed on this design as well.

Figures 7: Dimensioned Drawings of Version 2 Concept 3 using Solidworks (IPS units)

Details of the newly proposed prototype are displayed below in inches.

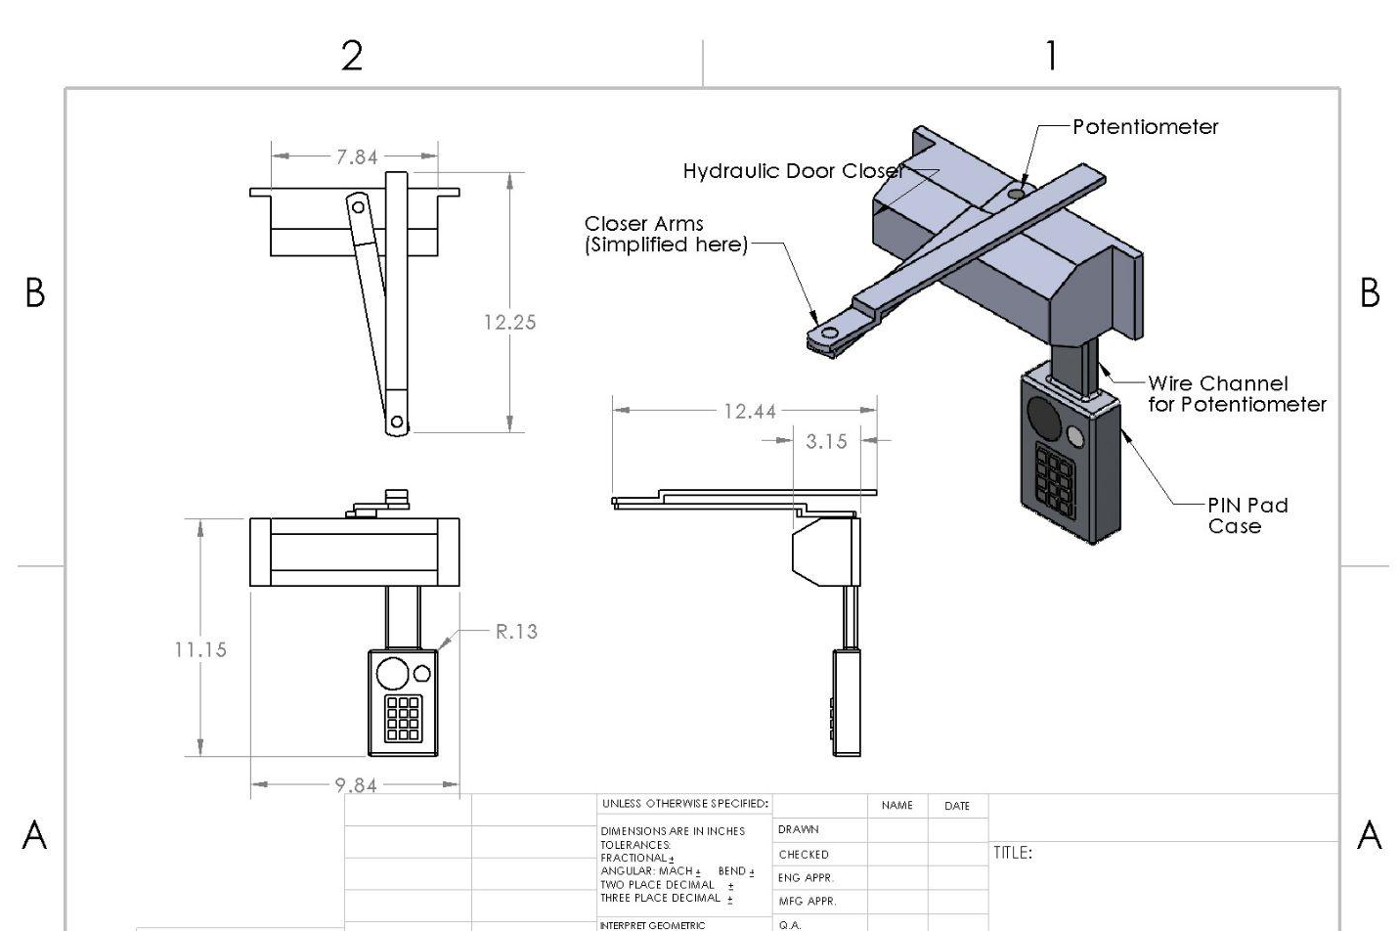
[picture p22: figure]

Figure 8: Dimensioned Drawings of Version 2 Concept 3 only Pin Pad component using Solidworks (IPS units)

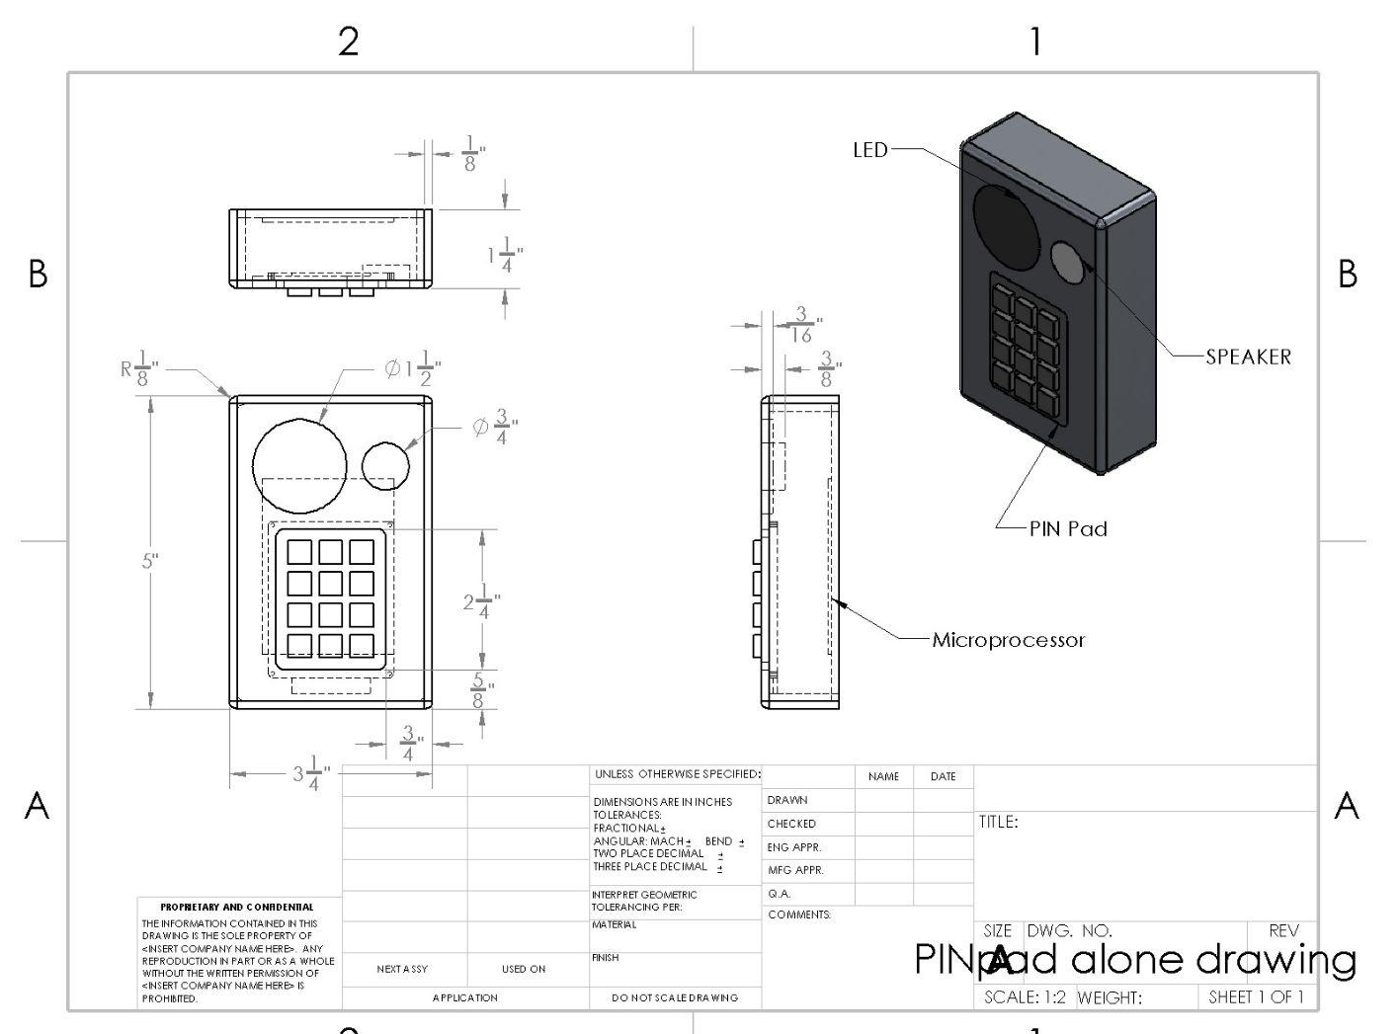
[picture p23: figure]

Figure 9: Wiring Schematic of Pin Pad, Potentiometer, Battery, Adafruit Metro, and LED

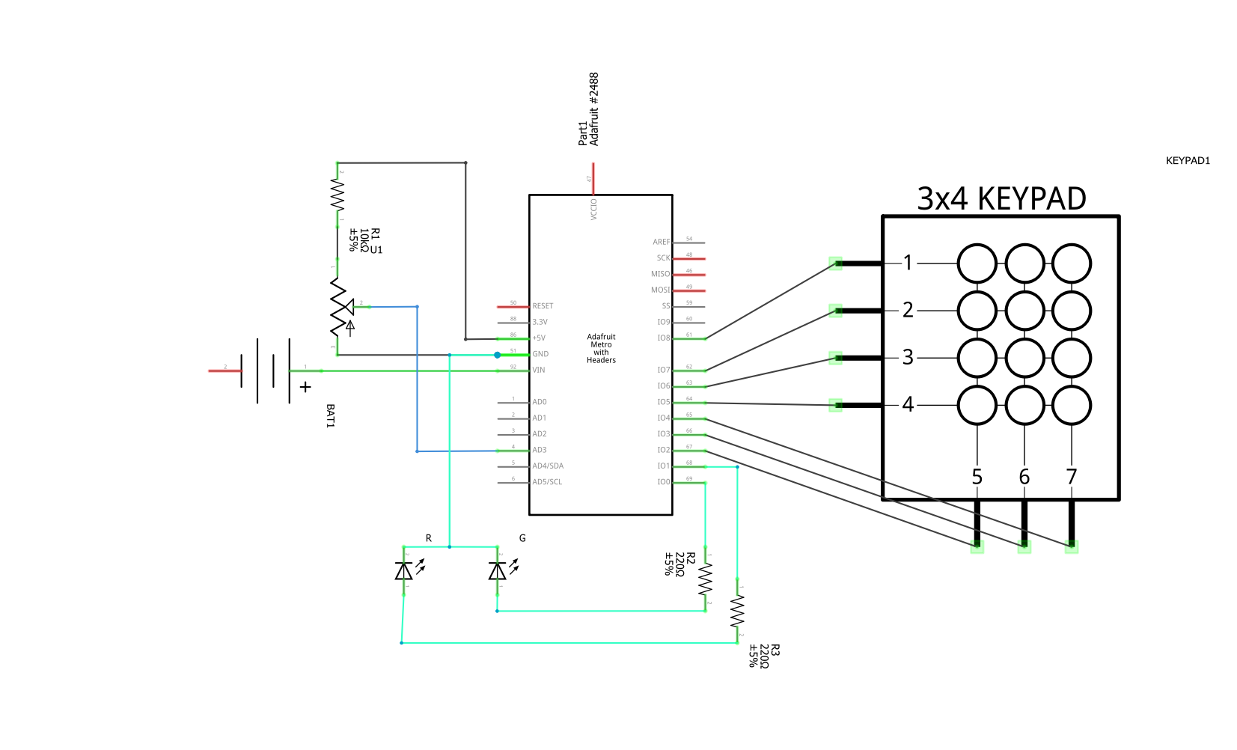
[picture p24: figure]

Figure 10: Exploded view of the closer part. Source from Cherry Wong [11]

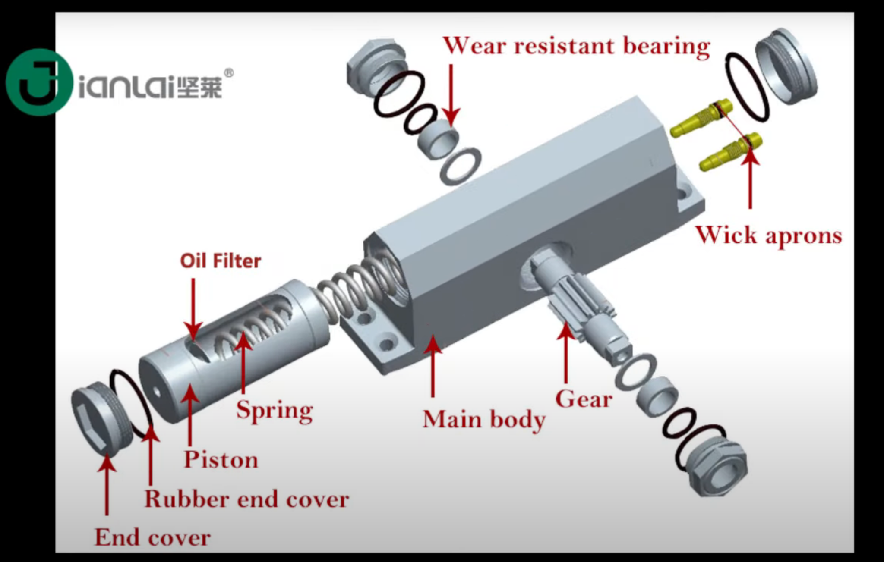
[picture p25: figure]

Figure 11:Dimensioned Drawings of Version Concept 3 only Pin Pad component using Solidworks (IPS units)

# References

[1]E. Coates, “Opto Switches,” Learnabout Electronics. Accessed: Jan. 21, 2024. [Online]. Available: https://learnabout-electronics.org/Semiconductors/opto_54.php

[2]“#01 What’s a Magnetic Sensor?,” Tutorials | Hall Sensors | Products | Asahi Kasei Microdevices (AKM). Accessed: Jan. 21, 2024. [Online]. Available: https://www.akm.com/content/www/akm/us/en/products/hall-sensor/tutorial/magnetic-sensor.html

[3]“Working principle of thermocouples,” https://www.omega.com/en-us/. Accessed: Jan. 21, 2024. [Online]. Available: https://www.omega.com/en-us/resources/how-thermocouples-work

[4]“What Is An Automatic Door Closer? | www.autodoorandhardware.com.” Accessed: Jan. 21, 2024. [Online]. Available: https://www.autodoorandhardware.com/What-Is-An-Automatic-Door-Closer--s/120992.htm

[5]“Cord Reels: Types, Configurations, Selection, and Requirements.” Accessed: Jan. 21, 2024. [Online]. Available: https://www.iqsdirectory.com/articles/hose-reel/cord-reels.html

[6]“All You Need to Know About Potentiometers,” CUI Devices. Accessed: Jan. 21, 2024. [Online]. Available: https://www.cuidevices.com/blog/all-you-need-to-know-about-potentiometers

[7]“Voltage Divider Circuits | Divider Circuits And Kirchhoff’s Laws | Electronics Textbook.” Accessed: Jan. 21, 2024. [Online]. Available: https://www.allaboutcircuits.com/textbook/direct-current/chpt-6/voltage-divider-circuits/

[8]jumpfactor, “What is RFID and how Does RFID Work?,” Lowry Solutions. Accessed: Jan. 21, 2024. [Online]. Available: https://lowrysolutions.com/blog/how-rfid-and-rfid-readers-actually-work/

[9]“How Does A Fingerprint Scanner Work — The Application Of Biometrics -.” Accessed: Jan. 21, 2024. [Online]. Available: https://www.biopanelsystems.co.uk/how-does-a-fingerprint-scanner-work-the-application-of-biometrics/

[10]“How Closers Internally Work | Norton Rixson Door Controls.” YouTube, YouTube, 1 June 2018, www.youtube.com/watch?v=ueKuYcvDQHQ.

[11]“How Hydraulic Door Closer Working Principle Inside (Jianlai Building Material Factory).” Youtube, Youtube, 3 Nov. 2020, https://www.youtube.com/watch?v=mXNhgCefKD8.

[12]“Firebase Cloud Messaging,” Firebase. Accessed: Jan. 21, 2024. [Online]. Available: https://firebase.google.com/docs/cloud-messaging

[13]B. Lockwood, “How to Stop Your LED Lights from Flickering,” Brennan Electric. Accessed: Jan. 21, 2024. [Online]. Available: (https://brennan-electric.com/how-to-stop-your-led-lights-from-flickering/)https://brennan-electric.com/how-to-stop-your-led-lights-from-flickering/

[14]“Feed Rate and Cutting Speed: Difference in CNC Machining - WayKen,” Rapid Prototype Manufacturing in China - WayKen. Accessed: Jan. 23, 2024. [Online]. Available: (https://waykenrm.com/blogs/feed-rate-and-cutting-speed-difference-in-cnc-machining/)https://waykenrm.com/blogs/feed-rate-and-cutting-speed-difference-in-cnc-machining/

# Appendix

## Interview With Steven Lucero

Q. What materials should be used for the housing and arm? Could they be the same material?

A. 6061 alloys for aluminum could work, though you have to be mindful of what machines you are using, for example, aluminum has to be machined. A variety of materials should probably be used. In the optimal parts of the design, sheetless cut stainless steel, 3D printed, and aluminum materials should be used.

Q. What parts could be 3D printed for rapid prototyping?

A. The case and arms could be done with PLA rapid prototyping while the interior would likely not be rapidly prototyped.

Q. Would it be possible to utilize the rotation about the arm joint with a rotational

potentiometer? How about using a slide inside the main housing?

A. It is possible to utilize the rotation about the arm joint with a rotational potentiometer or a rotary encoder. You could potentially make the wire longer so the joint can be more tolerant to movement. Furthermore, an idea to use in the design is a type of mechanical component that permits rotation with wires on either side called a slip ring.

Q. What are some potential mounting tactics we can use to ensure the components that need to stick together can stick?

A. Some mounting methods could be using adhesives, making the top wider for the surface area, epoxy weld possible if permanent, 3M, sticky form, or other products that could be searched. Furthermore, you might want to revisit the clip idea as a way to stick things together. Also, the idea of potentially sharing hardware with other fixtures should be thought of.

Q. What is the possibility of being able to adjust the height of the pinpad? Possible telescoping rod?

A. Being able to adjust the height of the pin pad is not really necessary.

Q. In order to make the arm able to contain a wire, how thick would the arm have to be?

A. You could keep the rotary on the top of the design potentially to contain the wire.

## Figure 10: User Needs Flowchart

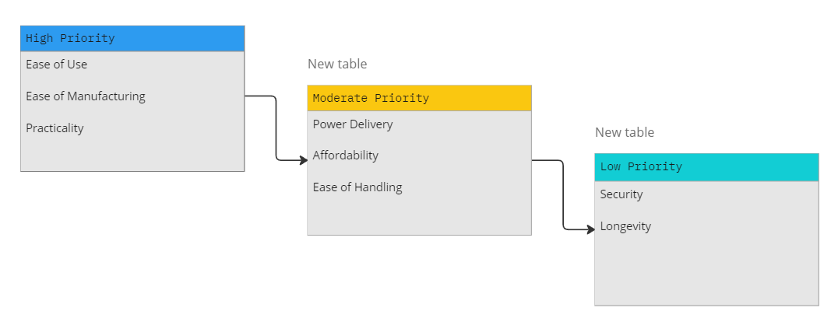
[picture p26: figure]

## Figure 11: Engineering Design Specifications

Metrics | Units | Corresponding User Needs | Range | Target Value | Direction of Improvement
Price | US Dollar | Affordability | $14-$984 | ≤ $300 | To be minimized
Battery Life | Weeks | Power Delivery | 1- ∞ | ≥ 8 | To be maximized
Passive Operation | Binary | Ease of Handling | Fully Active to Fully Passive | Mostly Passive | To be maximized
Number of Components | Numerical | Ease of Manufacturing | 10-100 | ≥ 20 | To be minimized
Established Technology | Binary | Practicality | Yes or No | Yes | N/A
Sensitivity | (TP)/(TP+FN) * | Security | 0-1 | ≥0.9 | To be maximized
Weight | Pounds | User Friendliness | 1 to 8 | 7 | To be minimized

[1] TP: True Positive

[2] FN: False Negative

## Figure 12: Milling Speeds Chart


Sourced from [14]

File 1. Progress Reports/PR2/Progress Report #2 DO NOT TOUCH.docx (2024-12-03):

Biorefrigerator Security System

Biomedical Engineering Senior Design

Dr. Aijun Wang

Progress Report 2

Winter 2024

Team 1

Problem and Objective 3

Problem 3

Objective 3

Concept Generation 4

Concept Generation Flow Chart 4

Primary Design Concepts 5

Concept Screening 8

Primary Screening 9

Secondary Screening 11

Materials and Manufacturability 12

Detail Drawings 13

Concept 1 13

Concept 3 14

Concept 2, Final Concept Chosen, Initial Design 15

References 15

Appendix 16

# Problem and Objective

## Problem

Current methods of ensuring that frequently accessed controlled laboratory environments remain closed are limited by the need for human input. Requiring the use of human input introduces the possibility of human error. In the case of currently used controlled laboratory environments, the most likely error is unintentionally leaving open controlled laboratory environments. This error can result in significant risk to the viability of materials within them, such as the denaturing of DNA or cells in the controlled environments.

## Objective

The objective of the Biorefrigerator Security System is to implement a device that minimizes the risk of sample deterioration due to prolonged exposure to ambient conditions. We aim for the device to be power efficient, affordable, easy to install, and easy to use. By both controlling and reporting the status of biological refrigerator doors, our device can be used by laboratory staff to autonomously close the doors.

Concept Generation

## Concept Generation Flow Chart

When we were looking and thinking about designing a device to help secure refrigerator doors, we started thinking about what should be considered in providing security and a way to keep the door closed or know when the door is open. We considered parts that could help with the device. The main two factors we considered were sensors and whether we should use digital components. We also realized that simple is better, as this would reduce the possibility of error. Our initial ideas only involved using the door, so therefore we decided to think about hinges. Overall, we realized that in order to decide what to design we should consider the best components to use and which to combine to provide the best concept to develop. By combining components and ideas that may cover for each other’s weaknesses, we could create a product that satisfies more of the criteria that we have set.


## Primary Design Concepts

When starting prototype ideas, when we looked back at our concept generation flow chart that we made, we realized that what we will prototype is based on many components that needed to be combined together. We realized that it would be good to make our first primary screening based on three components: detection, security, and alarm. We will have two primary screenings: Input, combining detection and security, and notification/alarm. Specific components we will screen are shown below and will have a description of why each component was considered.

Input(Status and Verification)
Detection | Security
Laser/Optical | Card
Magnetic | PinPad
Temperature | Finger Pad
Weighted
Wire
Angle Sensor

Alarm/Notification
Digital | Light Flashing
Sound Alarm | No Alarm

Component Section 1

All components listed below contribute to detection or remote signaling of door status..

Laser A laser sensor will help detect the open or closed status of the door by applying a laser to the door, which will constantly reflect back to a pad placed on the main part of the refrigerator. If the refrigerator door is open, then the laser will move with the door and leave the padding. Without the padding, reflection cannot occur and therefore the laser will detect that the door is open.

Magnetic A magnetic sensor will have two separate magnets: one on the door and one on the main compartment. When the magnets are together, then the connected magnets will enable the sensor to detect when the door is open.

Temperature A temperature sensor will be placed on the inside of the refrigerator. If the temperature increases past a certain point, then the sensor will detect that the refrigerator has been left open for too long.

Weighted

A weighted door will actively close the refrigerator door if the door is left open. The weighted system will pull the door closed.

Wire

A wire will be set somewhere between the refrigerator door and main compartment. If the wire is pulled too long, then the sensor will know that the door is left open. The wire can also help with closing the door as it will retract.

Angle Sensor

An angle sensor can be placed at the hinge of the door and can detect whether the door is open or closed if the sensor detects a high angle.

Component Section 2

The following components below are based on factors of security in order to check who opens the door whether specifically tied or a person or just anyone who has the information to open the door.

Card Reader

Most labs in UC Davis have a magnetic card for each person who works in a lab. We can use a card with the refrigerator lock to tell who is opening the door since cards have tracking systems that can be traced back to the user of the card.

PinPad

Using a PinPad can allow people who only know the password enter or have everyone have their own passcodes to know who specifically opens the refrigerator door.

Finger Pad

A finger pad sensor can be used to access the door while knowing who specifically opened the door with fingerprint authentication.

The following components are based on alarms or notifications. This can be used when the detection component notices the door is left open:

Digital

A digital notification would send an alert to the phone or computer of the administrator of the lab from an application. This solution necessitates either an internet connection or bluetooth connection. An internet connection would be preferred since it could work regardless of distance.

Sound Alarm

A sound alarm on the device can alert those in the area that a refrigerator had been left open and that the samples inside are prone to denaturing or being compromised.

Light Alarm

A light alarm on the device can provide an easy visual alert for a user to see that the refrigerator has not been shut all the way in order for the user to prevent the samples from degrading due to the refrigerator being open for too long.

No Alarm

Having no notification system could be feasible with solutions that guarantee the door closing when left open. Furthermore, it requires no extra materials. This solution comes with the downside that, should the closing device malfunction, no one would know without manually checking.

# Concept Screening

## Primary Screening


Looking at the primary screening, we rated each component based on the following criteria: power delivery, affordability, longevity, ease of use/user friendliness, ease of handling/accessibility, ease of manufacturing, practicality, and security. Each of these comes from an updated version of the User Needs Flowchart. To clarify the differences between ease of use and ease of handling, ease of use is a customer's ability to quickly understand how to use the product while ease of handling is a customer’s ability to physically interact with the product. Practicality is to determine whether previously devices using the component were used well or well received. Security, while initially thought to be highly prioritized, has significantly less weight as security has been proven to be high through other means. Overall, the ease of use and ease of manufacturing was set to have the highest weight. We want the customer to be able to quickly understand our product and we want to have easy manufacturing in order to have quick prototyping and quick reiterations of the device.

We divided all components into different colors categories: red, yellow, and green. The red category means that the component is poorly rated. After checking and talking with the team, the red components were not considered to move on to the secondary screening. The yellow categories could have been well-rated overall, but they will not move on to the secondary screening after proper deliberations between team members. For example, the wire system was highly rated, but it still seemed very intruding and obstructive to people wanting to open the door no matter where we placed it since a wire system would end up being tough to untangle and maneuver, and therefore, was moved to the yellow category. Finally, the green components were selected based on their high rating as well as being well received between team members and therefore, moved onto the secondary screening. Green-rated systems indicate that they are not too difficult to manufacture, take up a reasonable amount of space, and are intuitive methods for the user to interface with. Note that we did not blindly select random green components for our secondary screening, but rather deliberated over which components would work best in the green category. Overall, we made 3 prototype ideas to be put for the secondary screening.

## Secondary Screening


For our secondary screening, we created 3 concepts. We will go over these concepts in more detail in our detailed drawings sections where example designs are shown. To put simply, the first concept involved just the laser component, the second with the weighted door and pin pad, and third angle sensor and pin pad. All three concepts all include sound and light alarms. These concepts will be our initial prototypes for our devices and we will reiterate and change as we go. Selection criteria remained the same and the highest score of the three will not automatically be chosen as the prototype to work on, but rather deliberated over then chosen.

Result: Concept 2 was the best choice decided from our team. We took into account the scoring of the other concepts and deliberated rather than just accepting the highest score and going with that concept. Having the concept 2 prototype seems best as it actively closes the door meaning considering the door being left open is less likely. The alarms provided in the concept will be emergency alarms just in case the weighted door fails.

Overall, we realized that instead of checking the status of the door, we can instead work on changing the status of the door when it is in an unwanted state.

# Materials and Manufacturability

A couple of issues that arose from the initial design were the material choice, implementation of the rotary potentiometer, wiring, and methods of attachment. After meeting with Steven Lucero from the TEAM Lab, a few modifications were made to the initial design concept that we had created. In terms of the external design itself, not much was changed aside from the expansion of the surface that would connect to the top of the refrigerator. The manufacturing process of the finalized design will include the machining of aluminum for the body, as well as sheet cutting of stainless steel for thinner areas. Interior parts that do not experience significant stress will be 3D printed.

For the pin pad, we decided on a body that is made of 6061 aluminum as it is manufacturable and durable for the purposes of this project. We will have a microcontroller system in order to be able to get the code into the alarms, pin pad, and potentiometer system. A red and green LED light system will be installed on the outside of the device to signal the alarm status of the refrigerator door. We will have screws to attach various parts of the device. Permanent epoxy resin will be used in order to secure the final device to the refrigerator. PVC copper coating wires will be used as the wiring for the electronic components of the device, and these wires will be given enough length to allow for the movement of the arms. The closer will be modified in order to utilize the hydraulic components in the device for the closing action. The speaker will be placed inside the main housing body to act as an auditory alarm. A potentiometer will be used to measure the angle of the door to detect whether the door is open or not in the event that there is an obstruction. The arm of the device will be hollow and wide enough to house the rotary potentiometer in the rotational joint.

## Bill of Materials

Component | Material | Purchasing Location | Part Number | Quantity | Weight | Price Per Unit | Total Price | Notes | Link
6061 Aluminum | 6061 Aluminum | Amazon | N/A | 2 | 1.755 lbs per sheet | $18.99 | $37.98 | The body for the pin pad | 6061 Aluminum Component Link (https://www.amazon.com/Aluminium-Aluminum-Finely-Polished-Deburred/dp/B08M63VD66?hvadid=507685853899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)
Screws | 18-8 Stainless Steel | McMaster-Carr | 97613A529 | 1 | ~0 | $17.36 | $17.36 | For the Body attachment. 10 Pack | Screws (https://www.mcmaster.com/97613A529/)
Adafruit METRO | Microcontroller | Adafruit | 2488 | 1 | 0.042 lbs | $17.50 | $17.50 | Coding component for alarms, pin pad, potentiometer | Adafruit METRO (https://www.adafruit.com/product/2488)
Red and Green Indicator LED | LED | Adafruit | 4042 | 1 | Not Available | $1.75 | 1.75$ | Light Alarm | RED/GREEN LED Link (https://www.adafruit.com/product/4042)
Pin Pad | N/A | Adafruit | 3845 | 1 | ~0 | $6.50 | $6.50 | The pin pad itself | Pin Pad Link (https://www.adafruit.com/product/3845)
Wires | PVC Coated Copper | Amazon | B08BBXTBL7 | 1 | 0.79 lbs total | $14.94 | $14.94 | Wiring for the device | Wires (https://www.amazon.com/Gauge-Wire-Solid-Core-Hookup/dp/B08BBXTBL7?s=hi)
Potentiometer | Potentiometer | Adafruit | 562 | 1 | Not Available | $0.95 | $0.95 | 10k kiloohms | Potentiometer (https://www.adafruit.com/product/562)
Adhesive (Epoxy) | Epoxy Resin | Amazon | N/A | 1 | 0.125 lbs total | $12.45 | $12.45 | 2 pack, Metal Adhesive | Epoxy Resin (https://www.amazon.com/J-B-Weld-Original-Reinforced-Strength/dp/B0B5VNG2YT?hvadid=598238944920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)
Speaker | N/A | Adafruit | 1891 | 1 | 0.01 lbs | $1.75 | $1.75 | Speaker for the alarm | Speaker (https://www.adafruit.com/product/1891)
Closer | Aluminum | Amazon | ‎SOULONGg850ya231w | 1 | 2.31 lbs | $20.81 | $20.81 | Will use for hydraulic components | Closer Link (https://www.amazon.com/Aluminum-Commercial-Automatic-Closing-Independent/dp/B08GPD3W6V?hvadid=680463214693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)
Internal Brackets and other small parts | PLA | UC Davis | N/A | As needed | ~0 | Variable | Variable
Battery | 9V battery | Adafruit | 1959 | 1 | 0.17 lbs | $14.95 | $14.95 | Power source for device | https://www.adafruit.com/product/1959
Sum of Prices/Weights | | | | | ~6.9 lbs | | $131.99

## Purchasing

The components from the Bill of Materials will be purchased from their respective vendors, however some may also be sourced from preexisting stock at UC Davis in order to save time in shipping. The Bill of Materials is based on the current idea for the final design, and may be revised later on due to needs that have not arisen at this time.

## Rapid Prototyping

3D printing will be used for rapid prototyping of the design. PLA will be used in order to print the arms and main body of the case for prototyping purposes in order to minimize time and budget spent on machining. The dollar amount spent on 3D printing will vary depending on the amount of times revisions may need to be done, and thus this will be calculated and added to the finalized version of the Bill of Materials once prototyping has concluded.

# Detail Drawings

## Concept 1

Our first concept is a laser detector door opening device with a sound and light alarm, addressing the need to reduce the risk of contents in frequently accessed refrigerators from being compromised due to unexpected or prolonged access. The device employs a laser sensor, laser padding, and a light and sound box powered by AA batteries. By detecting the presence or absence of laser reflections off the padding, the sensor determines whether the refrigerator door is open. In the event of an open door, the device activates a light and sound alarm, alerting nearby individuals to the situation, and automatically deactivates when the door is closed. Despite concerns about security and longevity, the solution's quick and simple development, along with its ease of use, compensates for these drawbacks. The device's passive nature ensures minimal user interference, making it suitable for environments where active security measures may be impractical. Technical feasibility involves addressing precision challenges, exploring similar laser sensors, and identifying potential stimuli that could interfere, with an estimated prototype development and testing time of approximately four days. The solution's non-obvious and novel aspects include its passive operation and integration of alarm systems and laser sensors into a single physical unit, making it applicable in areas with limited network connectivity.


## Concept 3

The following concept involves the integration of an angle sensor at the hinge of a refrigerator door, coupled with a PinPad and alarm system to address the need for enhanced security in frequently accessed refrigerators. The PinPad allows users to input a code, disarming the alarms triggered by the Angle Sensor, which monitors the door's open and closed status through a potentiometer. If the door remains open beyond a specified time, the alarms activate with sound and flashing lights. The key components include a motherboard, PinPad with LED, potentiometer, and a speaker box with AA batteries. The angle sensor utilizes the potentiometer to measure electrical resistance, translating it into voltage readings corresponding to the door's angle. Pros include non-obtrusive installation at the hinge and providing a precise, nuanced measurement of door openness. However, concerns revolve around affordability, potential variations in refrigerator hinge designs, and power consumption. Technical feasibility is largely favorable, but questions about handling and power requirements need addressing. The concept's novelty lies in using a potentiometer for refrigerator security, offering a more nuanced approach than existing binary systems.


## Concept 2, Final Concept Chosen, Initial Design

The final and chosen concept to start working for prototyping addresses the need for enhanced security and automatic door closure in frequently accessed refrigerators. The design incorporates a weighted mechanism, utilizing a spring and sensor, to ensure reliable closure of the refrigerator door. A pin pad lock provides a secure means of access, allowing users to input a passcode for unlocking and locking the door. Additionally, a sound and light alarm system activates if the refrigerator is opened without the pin pad, requiring manual closure and passcode entry to disarm the alarm. The weighted mechanism serves a dual purpose, automatically closing the door after a specified time and acting as a failsafe in case of alarm-triggered failures. Despite potential concerns regarding ease of manufacturing, this concept excels in providing heightened security, ease of use, and practicality, addressing the critical need to prevent unauthorized access to the refrigerator's contents while not completely having to worry about the door being left open. These factors set it apart from previous prototypes, offering a unique and effective solution to enhance the overall security of frequently accessed refrigerators.


Version 2 of the weighted door design


# References

Links which we will base our weighted door design off of:

https://www.youtube.com/watch?v=ueKuYcvDQHQ

https://www.youtube.com/watch?v=mXNhgCefKD8

# Appendix

## Interview With Steven Lucero

Q. What materials should be used for the housing and arm? Could they be the same material?

A. 6061 alloys for aluminum could work, though you have to be mindful of what machines you are using, for example, aluminum has to be machined. A variety of materials should probably be used. In the optimal parts of the design, sheetless cut stainless steel, 3D printed, and aluminum materials should be used.

Q. What parts could be 3D printed for rapid prototyping?

A. The case and arms could be done with PLA rapid prototyping while the interior would likely not be rapidly prototyped.

Q. Would it be possible to utilize the rotation about the arm joint with a rotational

potentiometer? How about using a slide inside the main housing?

A. It is possible to utilize the rotation about the arm joint with a rotational potentiometer or a rotary encoder. You could potentially make the wire longer so the joint can be more tolerant to movement. Furthermore, an idea to use in the design is a type of mechanical component that permits rotation with wires on either side called a slip ring.

Q. What are some potential mounting tactics we can use to ensure the components that need to stick together can stick?

A. Some mounting methods could be using adhesives, making the top wider for the surface area, epoxy weld possible if permanent, 3M, sticky form, or other products that could be searched. Furthermore, you might want to revisit the clip idea as a way to stick things together. Also, the idea of potentially sharing hardware with other fixtures should be thought of.

Q. What is the possibility of being able to adjust the height of the pinpad? Possible telescoping rod?

A. Being able to adjust the height of the pin pad is not really necessary.

Q. In order to make the arm able to contain a wire, how thick would the arm have to be?

A. You could keep the rotary on the top of the design potentially to contain the wire.

## User Needs Flowchart


## Engineering Design Specifications

Metrics | Units | Corresponding User Needs | Range | Target Value | Direction of Improvement
Price | US Dollar | Affordability | $14-$984 | ≤ $300 | To be minimized
Battery Life | Weeks | Power Delivery | 1- ∞ | ≥ 8 | To be maximized
Passive Operation | Binary | Ease of Handling | Fully Active to Fully Passive | Mostly Passive | To be maximized
Number of Components | Numerical | Ease of Manufacturing | 10-100 | ≥ 20 | To be minimized
Established Technology | Binary | Practicality | Yes or No | Yes | N/A
Sensitivity | (TP)/(TP+FN) * | Security | 0-1 | ≥0.9 | To be maximized
Weight | kg | User Friendliness | 1 kg to 4 kg | 2 kg | To be minimized

[1] TP: True Positive

[2] FN: False Negative

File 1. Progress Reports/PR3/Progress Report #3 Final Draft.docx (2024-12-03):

Biorefrigerator Security System

Biomedical Engineering Senior Design

Dr. Aijun Wang

Progress Report 3

Winter 2024

Team 1

Brayden Chipman - 3/8/24 7:48 PM

Miguel Cruz - 3/8/24 6:17 PM

Ashwin Halepet - 3/8/24, 5:36 PM

Vance Padilla -3/8/24, 8:24 PM

Table of Contents

Problem and Objective 2

Problem Statement 2

Design Objective 3

Design Solution 3

Design Updates 3

Verification and Validation 4

Recognized Consensus Standards 5

Standards to Meet 5

Verification 6

Verification Process Flow 6

Individual Component Verification 7

Subsystem Device Verification 10

Validation 12

Future Development/Small Scale Development 13

Large-Scale Validation 14

Preliminary Hazards Analysis 15

Failure Modes and Effects Analysis (FMEA) 15

FMEA Analysis/Discussion 19

Risk Mitigation Strategies 20

Societal Impact 21

Value Proposition 21

Ethical Considerations 21

Green Engineering 22

Regulatory Pathway 23

References 25

Appendix 26

Figure 6: House of Quality 26

Preliminary Verification Test Protocols 27

Figure 7: Circuitry Diagram 32

Table 6: Complete Failure Modes and Effects Analysis 33

Table 7: Engineering Design Specifications 37

Table 8: Bill of Materials 38

# Problem and Objective

Figure 1: Introductory Figure for the Design


We are 3rd and 4th year students enrolled in UC Davis’ BIM 110, “Biomedical Engineering Senior Design”. We have been assigned to work on a project proposed to us by Dr. Aijun Wang and PhD candidate Yongheng Wang. Over the last two quarters, we have developed the Biorefrigerator Security System depicted above. This device’s function is to prevent the loss of biological samples that are stored in a controlled laboratory environment (CLE), such as a -20 C or -40 C freezer, thus preventing the associated monetary loss that results from the loss of samples. This device works by using a passive, hydraulic door closer to prevent the CLE door from not fully closing. Furthermore, this device also has a PIN pad to ensure that only members of the lab who are using the CLE can access the samples. Additionally, the device has an alarm system to alert users that either an event of unauthorized access occurred, or if the door is propped open.

## Problem Statement

Current methods of ensuring that a frequently accessed CLE remains closed are limited by the need for human input. Humans typically interact with the CLE by opening or closing the doors manually. Requiring the use of human input introduces the possibility of human error. Some newer models of CLE’s have methods to signal that they are left open such as audible alarms. However, older CLE models may not have a method to signal that they are accidentally left open. The most common error of human input in CLE’s is accidentally leaving them open. Exposure to room-temperature should be minimized and have been proven to negatively affect biological material, especially proteins, over time. For example, even short periods of thawing and refreezing can lead to mild denaturing and minor loss of proteins. Ten cycles of thawing and refreezing already show at least over 5% loss of many types of proteins [1]. Ideally, it would be best to prevent this situation from constantly occurring because the loss of integrity can then lead to time and monetary loss.

## Design Objective

The objective of the Biorefrigerator Security System is to develop a device that minimizes the risk of sample deterioration due to prolonged exposure to ambient conditions. We aim for the device to be power efficient, affordable, easy to install, and easy to use. Primary intended use cases are CLEs such as chemical and biological laboratory refrigerators, as well as incubators.
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

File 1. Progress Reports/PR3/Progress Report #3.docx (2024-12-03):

Biorefrigerator Security System

Biomedical Engineering Senior Design

Dr. Aijun Wang

Progress Report 3

Winter 2024

Team 1

Brayden Chipman -

Miguel Cruz -

Ashwin Halepet -

Vance Padilla -

Table of Contents

Problem and Objective 2

Problem Statement 2

Design Objective 2

Design Solution 3

Verification and Validation 4

Recognized Consensus Standards 4

Verification 4

Verification Process Flow 4

Individual Component Verification 5

System Device Verification 8

Validation 9

Future Development/Small Scale Development 10

Large Scale Validation 10

Preliminary Hazards Analysis 11

Failure Modes and Effects Analysis (FMEA) 11

FMEA Analysis/Discussion 15

Risk Mitigation Strategies (Optional) 15

Societal Impact 16

Value Properties 16

Ethical Considerations 16

Green Engineering 17

Regulatory Pathway 18

References 20

Appendix 21

House of Quality 21

Standards to Meet 22

Verification Test Protocols 22
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

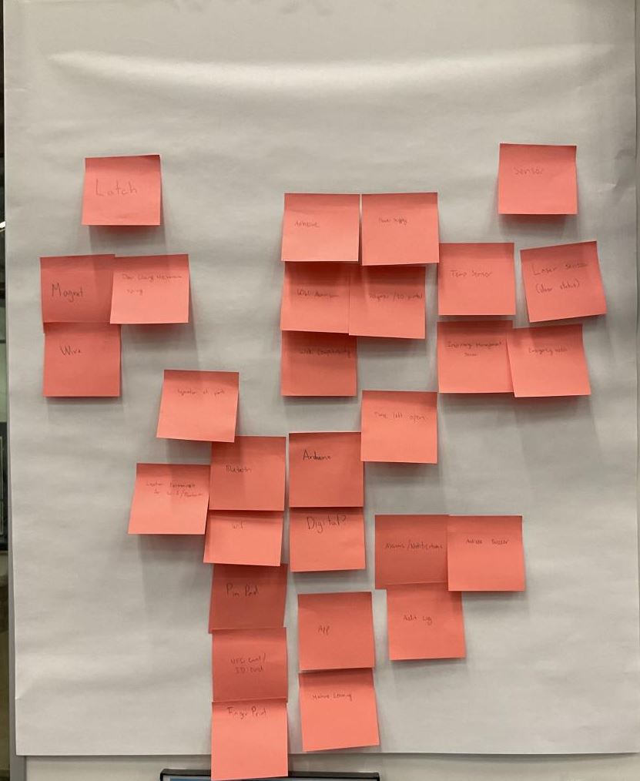
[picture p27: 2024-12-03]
9. Testing Plans and Data (Drawings, Revision History File, Screening)/Drawings/Initial Concepts/Concept Post It Notes.JPG

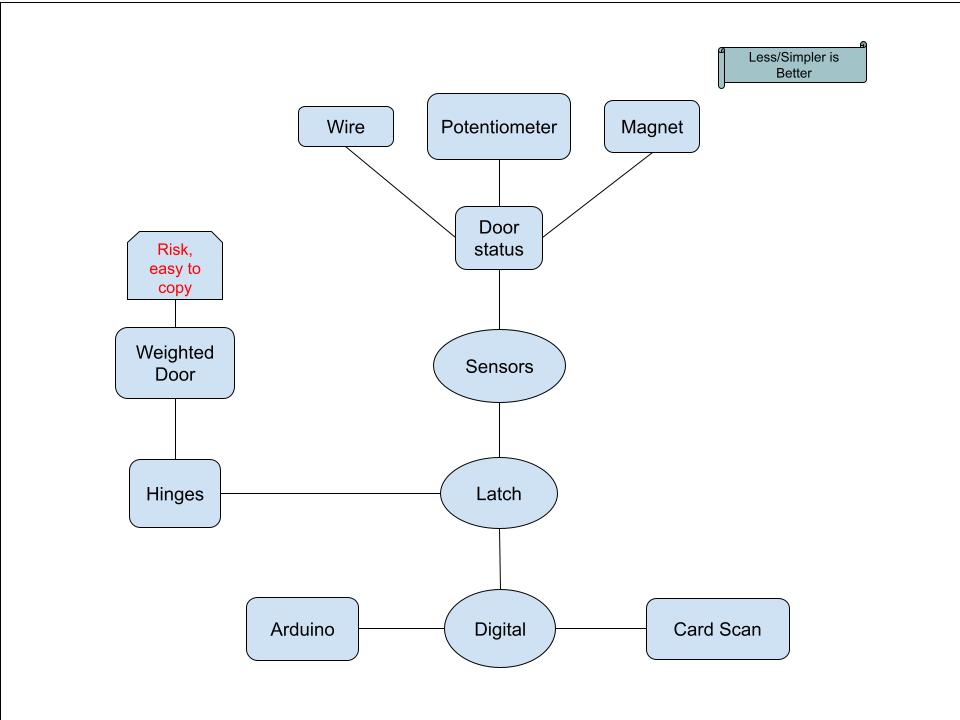
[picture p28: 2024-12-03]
9. Testing Plans and Data (Drawings, Revision History File, Screening)/Drawings/Initial Concepts/Flowchart.jpg

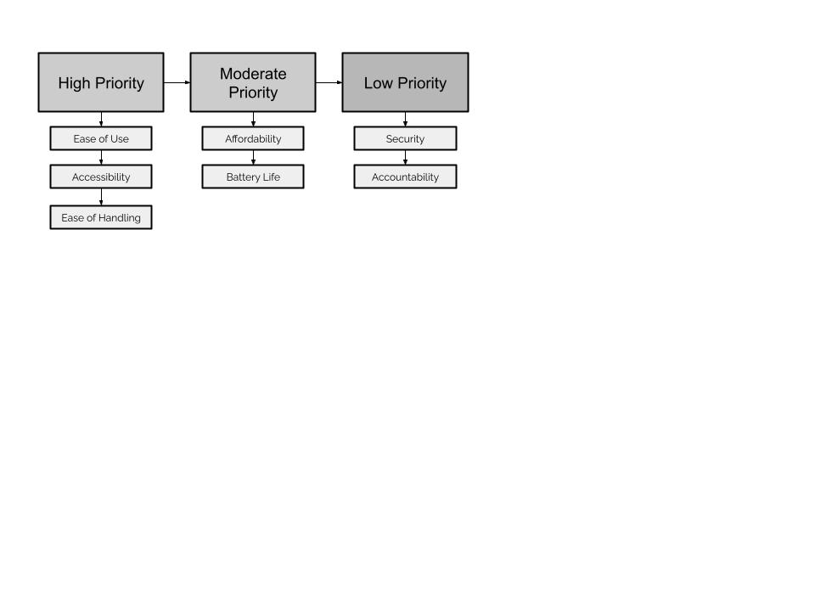
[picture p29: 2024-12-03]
10. Reference Materials (User Needs Survey, Benchmarking, EDS, HOQ, AI Log, User Needs Survey)/User Needs Survey/User Needs flowchart v3.jpg

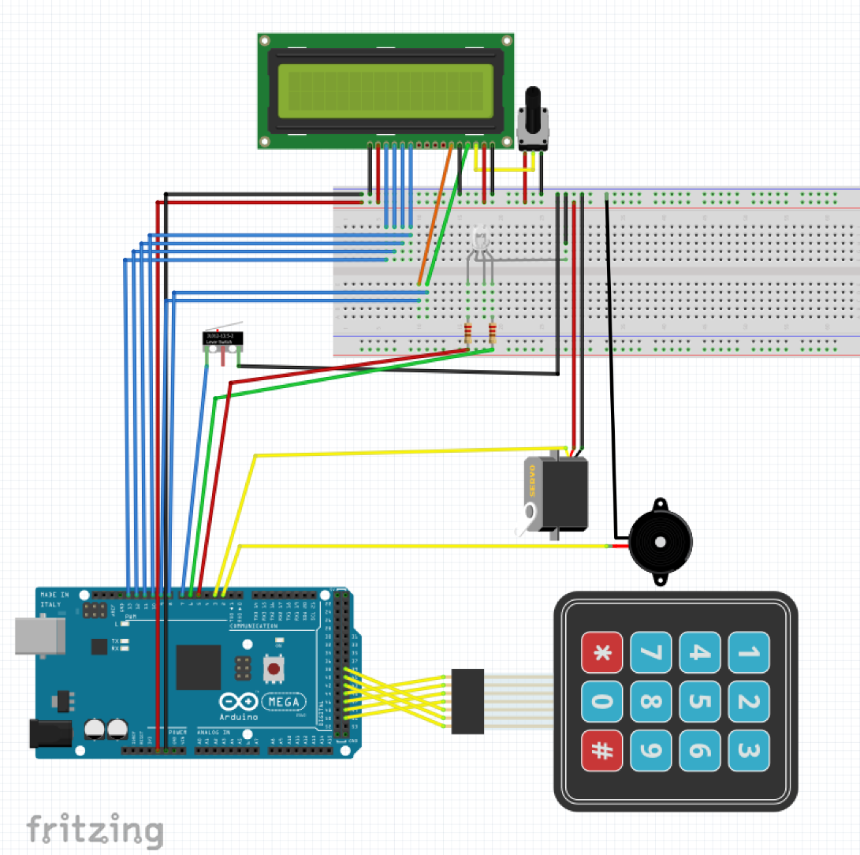
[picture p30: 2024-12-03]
6. Circuit Files/Arduiono Code and Fritzing Diagram/Fritzing Diagram.PNG

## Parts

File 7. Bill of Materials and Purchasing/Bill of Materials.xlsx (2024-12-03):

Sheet: Bill of Materials
Component | Material | Purchasing Location | Part Number | Quantity | Weight | Price Per Purchase | Total Price | Notes | Link | Purchased by AW | Recieved | 05Apr re-purchase
Case | PLA | UC Davis | N/A | Per kg | ~1/2 kg | $30 per kg | $15
Screws | 18-8 Stainless Steel | McMaster-Carr | 92010A216 | 1 pack | ~0 | $7.01 | $7.01 | For the Body attachment. 100 Pack | Screws (https://www.mcmaster.com/92010A216/) | x | x
6061 Aluminum | 6061 Aluminum | Amazon | N/A | 3 | 1.755 lbs per sheet | $18.99 | $56.97 | The body for the pin pad | 6061 Aluminum Component Link (https://www.amazon.com/Aluminium-Aluminum-Finely-Polished-Deburred/dp/B08M63VD66?hvadid=507685853899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) | x | x
Wires | PVC Coated Copper | Amazon | B08BBXTBL7 | 1 | 0.79 lbs total | $14.94 | $14.94 | Wiring for the device | Wires (https://www.amazon.com/Gauge-Wire-Solid-Core-Hookup/dp/B08BBXTBL7?s=hi) | x | x
Adhesive (Epoxy) | Epoxy Resin | Amazon | N/A | 1 | 0.125 lbs total | $12.45 | $12.45 | 2 pack, Metal Adhesive | Epoxy Resin (https://www.amazon.com/J-B-Weld-Original-Reinforced-Strength/dp/B0B5VNG2YT?hvadid=598238944920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) | x | x
Closer | Aluminum | Amazon | ‎SOULONGg850ya231w | 1 | 2.31 lbs | $20.81 | $20.81 | Will use for hydraulic components | Closer Link (https://www.amazon.com/Aluminum-Commercial-Automatic-Closing-Independent/dp/B08GPD3W6V?hvadid=680463214693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) | x | x
Limit Switch | metal and plastic | Amazon | V-156-1C25 | 10 | Not Available | $1.00 | $9.99 | Possible to use in place of potentiometer, will test | Limit Switch (https://a.co/d/gz5lPw8) | x | x
Battery | 9V battery | Amazon | N/A | 1 pack of 4 | 0.05lbs | $9.55 | $9.55 | Power source for device | 9V battery (https://www.amazon.com/Amazon-Basics-Performance-All-Purpose-Batteries/dp/B0774D64LT?th=1) | x | x
18 Gauge Steel Sheet | Mild Steel | Amazon | B08GFXMXNG | 2 packs of 2 | 2.84 lbs per sheet | $29.90 | $59.80 | Alternative Body for case | https://a.co/d/a3CqhTq | x | x
Adafruit METRO | Microcontroller | Adafruit | 3505 | 1 | 0.042 lbs | $17.50 | 17.50$ | Coding component for alarms, pin pad, potentiometer | Adafruit METRO (https://www.adafruit.com/product/3505) | x | x
Red and Green Indicator LED | LED | Adafruit | 4042 | 1 | Not Available | $1.75 | $1.75 | Light Alarm | RED/GREEN LED Link (https://www.adafruit.com/product/4042) | x | x | Out of stock, new listing required
Pin Pad | N/A | Adafruit | 3845 | 2 | ~0 | $6.50 | $13.00 | The pin pad itself | Pin Pad Link (https://www.adafruit.com/product/3845) | x | x | x
Potentiometer | metal | Adafruit | 562 | 1 | Not Available | $0.95 | $0.95 | 10k kiloohms | Potentiometer (https://www.adafruit.com/product/562) | x | x
Speaker | N/A | Adafruit | 1891 | 2 | 0.01 lbs | $1.75 | $3.50 | Speaker for the alarm | Speaker (https://www.adafruit.com/product/1891) | x | x | x
Resistor | 10kΩ 5% | Adafruit | 2784 | 2 | ~0 | $0.75 | $1.50 | For voltage divider | 10kΩ resistor (https://www.adafruit.com/product/2784) | x | x | x
Battery Holder |  | Adafruit | 67 | 2 | 0.05lbs | $3.95 | $7.90 |  | https://www.adafruit.com/product/67 | x | x | x
Servo | Micro Servo | Adafruit | 2307 | 2 | 0.03lbs | $11.95 | $23.90 |  | Servo (https://www.adafruit.com/product/2307) | x | x | x
Metro ESP32-S3 | Microcontroller | Adafruit | 5500 | 1 |  | $24.95 | $24.95 |  | Metro ESP32-S3 (https://www.adafruit.com/product/5500) | x | x | x
LCD Backlight | LCD Display | Adafruit | 181 | 2 | Neglible | $9.95 | $19.90 | Possible HUD | https://www.adafruit.com/product/181 | x | x | x
Female/Male Jumper Wire | Silicone Covered | Adafruit | 1953 | 1 | ~0.03lbs | $1.95 | $1.95 | F/M Extension - 20 x 6" (150mm) | https://www.adafruit.com/product/1954
Male/Male Jump Wire | Silicone Covered | Adafruit | 4482 | 1 | 0.03lbs | $1.95 | $1.95 | M/M Extension - 20 x 6" (150mm) | https://adafruit.com/product/1957
ELEGOO MEGA 2560 | Microcontroller | ELEGOO | N/A | 1 |  | $19.99 | $19.99 | Microntroller used in the prototype | ELEGOO (https://www.elegoo.com/products/elegoo-mega-2560-r3-board)
18 Gauge Steel Sheet | Mild Steel | Amazon | B08GFXMXNG | 1 | 1.42 lbs per sheet | $29.90 | $29.90 | Attachment Block | https://a.co/d/a3CqhTq
Self Tapping Screws | Stainless Steel | Amazon | 9015995 | 1 pack | ~0 | $6.90 | $6.90 | For component attachment. 25 Pack | Screws (https://a.co/d/gUcn6Kk)
6-32 Hex Nuts | Zinc Plated Steel | Home Depot | 802131 | 6 | ~0 | $1.38 | $1.38 |  | Hex Nuts (https://www.homedepot.com/p/Everbilt-6-32-Zinc-Plated-Machine-Screw-Nut-12-Pack-802131/204274121?locale=en-US&pla&gad_source=1&gclsrc=aw.ds)
Mini Breadboard | Plastic | Amazon | EK2137 | 2 | 0.01 lbs | $8 | $8.00 |  | Mini Breadboard (https://www.amazon.com/dp/B0146MGBWI?starsLeft=1)
Sum of Prices |  |  |  |  |  |  | $391.44
 |  |  |  |  |  | Remaining Budget = | $208.56

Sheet: Final BoM
Component | Material | Purchasing Location | Part Number | Quantity | Weight | Price Per Purchase | Total Price | Notes | Link
Case | PLA | UC Davis | N/A | 1 | ~1/2 kg | $30 per kg | $15
18 Gauge Steel Sheet | Mild Steel | Amazon | B08GFXMXNG | 1 | 1.42 lbs per sheet | $29.90 | $29.90 | Attachment Block | https://a.co/d/a3CqhTq
Screws | 18-8 Stainless Steel | McMaster-Carr | 92010A216 | 1 | ~0 | $7.01 | $7.01 | For the Body attachment. 100 Pack | Screws (https://www.mcmaster.com/92010A216/)
Wires | PVC Coated Copper | Amazon | B08BBXTBL7 | 1 | 0.79 lbs total | $14.94 | $14.94 | Wiring for the device | Wires (https://www.amazon.com/Gauge-Wire-Solid-Core-Hookup/dp/B08BBXTBL7?s=hi)
Adhesive (Epoxy) | Epoxy Resin | Amazon | N/A | 1 | 0.125 lbs total | $12.45 | $12.45 | 2 pack, Metal Adhesive | Epoxy Resin (https://www.amazon.com/J-B-Weld-Original-Reinforced-Strength/dp/B0B5VNG2YT?hvadid=598238944920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)
Closer | Aluminum | Amazon | ‎SOULONGg850ya231w | 1 | 2.31 lbs | $20.81 | $20.81 | Will use for hydraulic components | Closer Link (https://www.amazon.com/Aluminum-Commercial-Automatic-Closing-Independent/dp/B08GPD3W6V?hvadid=680463214693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)
Limit Switch | metal and plastic | Amazon | V-156-1C25 | 1 | Not Available | $1.00 | $1.00 |  | Limit Switch (https://a.co/d/gz5lPw8)
Battery | 9V battery | Amazon | N/A | 1 | 0.05lbs | $9.55 | $9.55 | Power source for device | 9V battery (https://www.amazon.com/Amazon-Basics-Performance-All-Purpose-Batteries/dp/B0774D64LT?th=1)
Red and Green Indicator LED | LED | Adafruit | 4042 | 1 | Not Available | $1.75 | $1.75 | Light Alarm | RED/GREEN LED Link (https://www.adafruit.com/product/4042)
Pin Pad | N/A | Adafruit | 3845 | 1 | ~0 | $6.50 | $6.50 | The pin pad itself | Pin Pad Link (https://www.adafruit.com/product/3845)
Speaker | N/A | Adafruit | 1891 | 1 | 0.01 lbs | $1.75 | $1.75 | Speaker for the alarm | Speaker (https://www.adafruit.com/product/1891)
Resistor | 10kΩ 5% | Adafruit | 2784 | 1 | ~0 | $0.75 | $0.75 | For voltage divider | 10kΩ resistor (https://www.adafruit.com/product/2784)
Battery Holder |  | Adafruit | 67 | 1 | 0.05lbs | $3.95 | $3.95 |  | https://www.adafruit.com/product/67
Servo | Micro Servo | Adafruit | 2307 | 1 | 0.03lbs | $11.95 | $11.95 |  | Servo (https://www.adafruit.com/product/2307)
ELEGOO MEGA 2560 | Microcontroller | ELEGOO | N/A | 1 |  | $19.99 | $19.99 | Microntroller used in the prototype | ELEGOO (https://www.elegoo.com/products/elegoo-mega-2560-r3-board)
LCD Backlight | LCD Display | Adafruit | 181 | 1 | Negligible | $9.95 | $9.95 | Possible HUD | https://www.adafruit.com/product/181
Female/Male Jumper Wire | Silicone Covered | Adafruit | 1953 | 1 | ~0.03lbs | $1.95 | $1.95 | F/M Extension - 20 x 6" (150mm) | https://www.adafruit.com/product/1954
Male/Male Jump Wire | Silicone Covered | Adafruit | 4482 | 1 | 0.03lbs | $1.95 | $1.95 | M/M Extension - 20 x 6" (150mm) | https://adafruit.com/product/1957
Sum of Prices |  |  |  |  |  |  | $171.15

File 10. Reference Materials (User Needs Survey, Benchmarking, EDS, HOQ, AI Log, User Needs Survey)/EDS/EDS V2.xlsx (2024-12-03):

Metrics | Units | Corresponding User Needs | Range | Target Value | Direction of Improvement
Price | US Dollar | Affordability | $14-$984 | $300 | To be minimized
Battery Life | Months | Power Delivery | 1- | 6 | To be maximized
Passive Operation | Binary | Ease of Handling | Fully Active to Fully Passive | Mostly Passive | To be maximized
Number of Components | Numerical | Ease of Manufacturing | 10-100 | 20 | To be minimized
Established Technology | Binary | Practicality | Yes or No | Yes | N/A
Weight | Pounds | User Friendliness | 1 to 8 | 7 | To be minimized
Miguel Cruz | 2024-04-22 | 21:49:00

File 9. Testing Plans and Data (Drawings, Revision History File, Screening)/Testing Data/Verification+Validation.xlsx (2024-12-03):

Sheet: Individual Components
Component | Simplified Test Method | Data | Data Analysis Method | Result Analysis Method | Result Analysis | Pass/No Pass
Battery | Measure battery voltage | 9.68, 9.69, 9.68 | average and standard devition | Mean ≥ 9 V | Standard Dev. ≤ 0.225 V | Mean: 9.683 V Standard Dev. 0.005 V | PASS
Microcontroller | "Hello World" Arduino Protocol | Funtional | Binary: functional or nonfunctional | n/a | n/a | PASS
Red and Green LED | Input voltage to green and red LED pins | Funtional | Binary: functional or nonfunctional | n/a | n/a | PASS
Speaker | release alarm sound of 1000 to check for audibility at conversational volume | Funtional | Binary: functional or nonfunctional | n/a | n/a | PASS
Limit Switch | Attach limit switch to microcontroller. Change in input reading is expected when the lever is pressed | Funtional | Binary: functional or nonfunctional | n/a | n/a | PASS
LCD Screen | Display the "Hello World" Arduino Protocol | Funtional | Binary: functional or nonfunctional | n/a | n/a | PASS
Pressurized Door Closer | Pull back the arm of the Door Closer and examine if it returns to the original postion when released | Funtional | Binary: functional or nonfunctional | n/a | n/a | PASS

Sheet: Subsystems
Subsystem | Simplified Test Method | Result Analysis Method | Result Analysis | Pass/No Pass
Alarm System 1 | Press down the lever on the limit switch then release for 2 seconds. Both alarms should trigger. | Binary: functional or nonfunctional | n/a | PASS
Alarm System 2 | Input the PIN Code "77777777". Both alarms should trigger | Binary: functional or nonfunctional | n/a | PASS
PIN Pad and Lock 1 | Input the PIN Code "1234567". Servo arm should rotate 90 degrees clockwise in the locked state and 90 degrees counterclockwise in the open state | Binary: functional or nonfunctional | n/a | PASS

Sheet: Full Assembly
Metric | Test | Result
Final Cost
Final Weight
Battery Life
Ease of Use
Ease of Handling
Security

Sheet: Validation
Component | Simplified Test Method | Scale (If Needed) | Result Analysis Method | Result Analysis | Pass/No Pass
Final Cost | Sum of used parts in USD | n/a | Sum < 200 is considered a "pass"
Final Weight | Weigh final assembly with a scale in pounds | n/a | Final Weight =< 7 pounds is considered a "pass"
Battery Life | Measure average hourly voltage usage and calculate approximate battery life | n/a | Battery life >= 6 months
Ease of Use | Qualitative: Users given a survey to rate understanding of device usage | fully intuitive --> some guidence needed --> training required | Some guidence needed is considered a "pass"
Ease of Handling | Qualitative: Users will be given a survey to rate if the device makes the CLE more difficult to operate or not | no difference--> slightly more difficult--> moderately more difficult--> much more difficult | Slightly more difficult to operate is considered a " pass"
Security | Measure force required to make the hook lock detach from the servo | n/a | Binary: functional or nonfunctional
Accountability | Future development: Give users unique PIN codes and store the most recently used | n/a | Binary: functional or nonfunctional

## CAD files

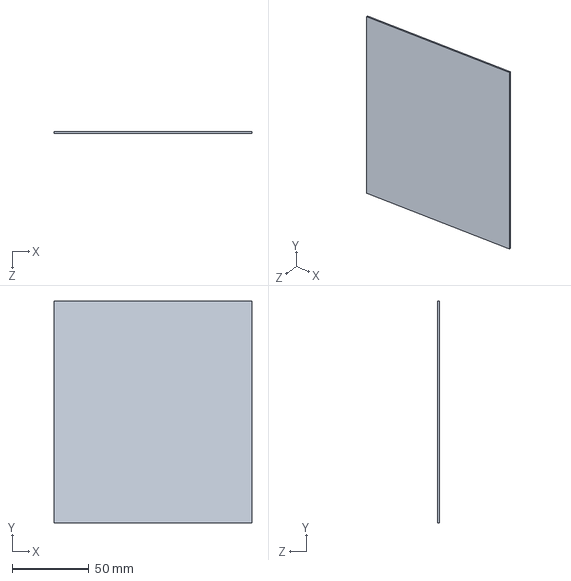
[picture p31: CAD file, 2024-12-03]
5. CAD Files/Circuitry Files/Final Design/Back Panel Main.SLDPRT
128.6 x 144.5 x 1.21 mm

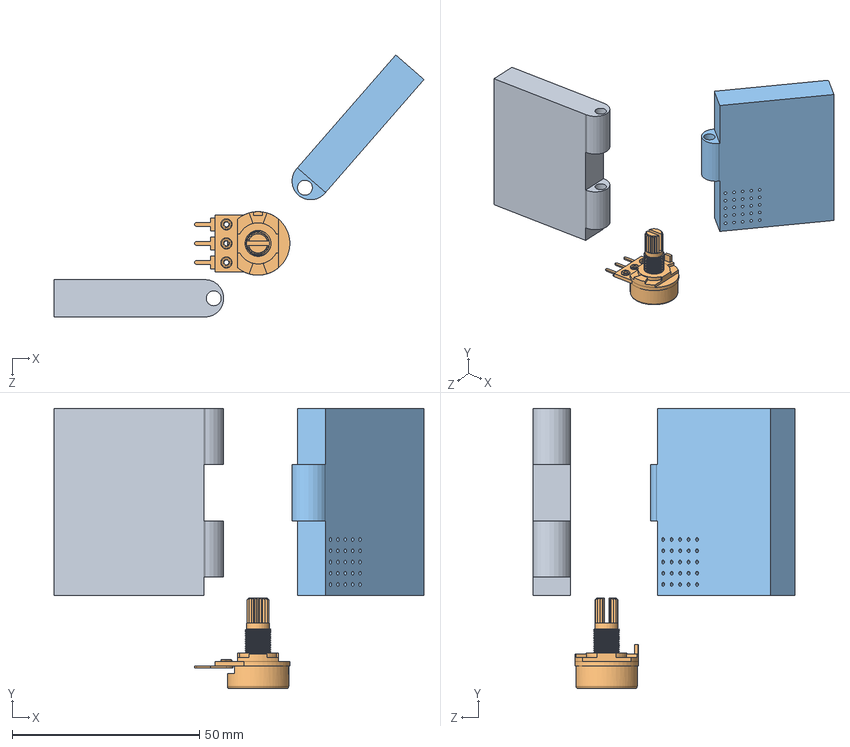
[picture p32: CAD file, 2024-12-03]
5. CAD Files/Initial Designs/angle sensor design.SLDASM
98.8 x 74.8 x 70.0 mm
pinpad
POT10K
speaker side

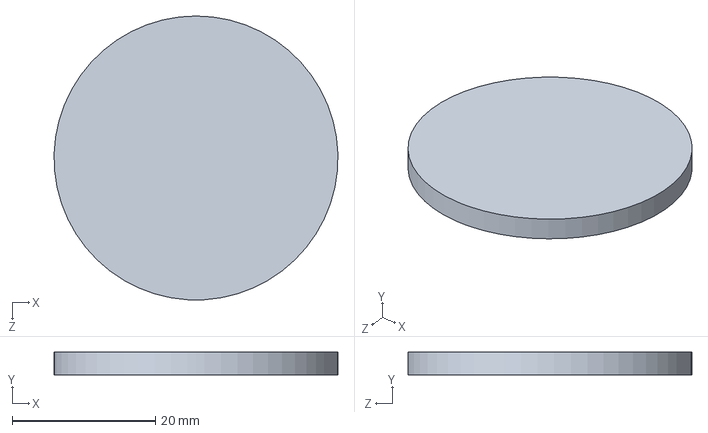
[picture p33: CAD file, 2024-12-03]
5. CAD Files/Circuitry Files/Basic Shapes/speaker.SLDPRT
39.7 x 3.17 x 39.7 mm

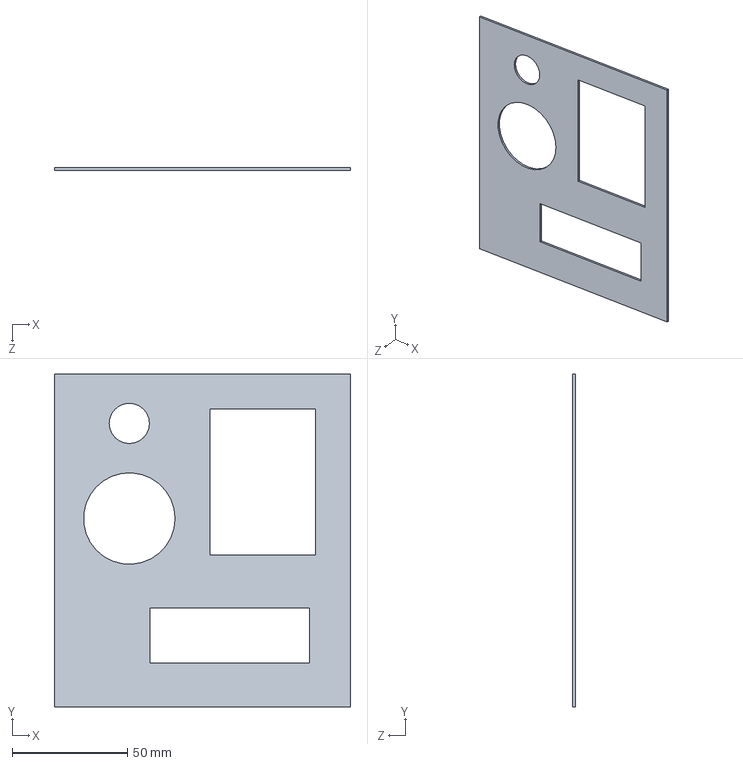
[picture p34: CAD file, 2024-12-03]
5. CAD Files/Circuitry Files/Final Design/Front Panel.SLDPRT
128.6 x 144.5 x 1.21 mm

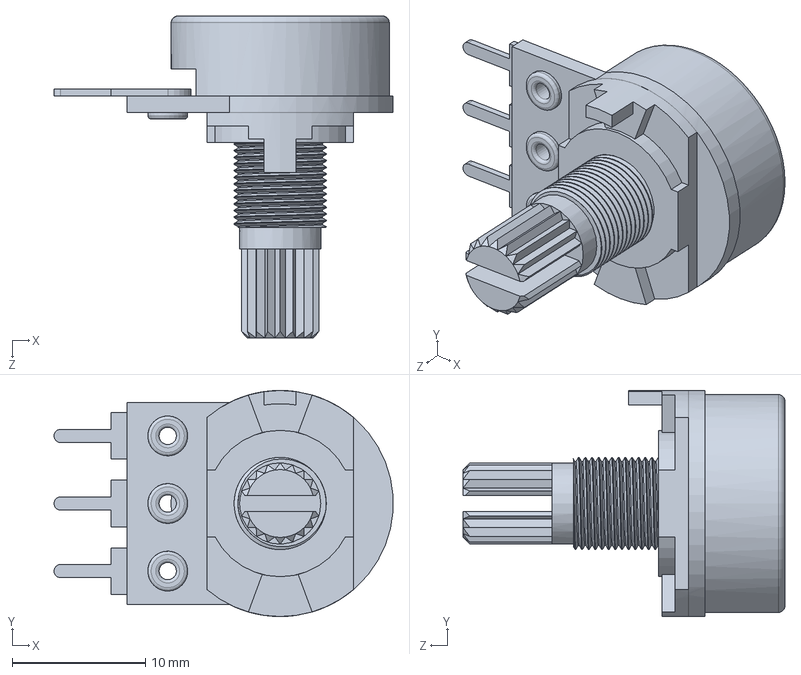
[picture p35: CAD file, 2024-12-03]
5. CAD Files/Initial Designs/POT10K.SLDPRT
25.5 x 17.0 x 24.2 mm

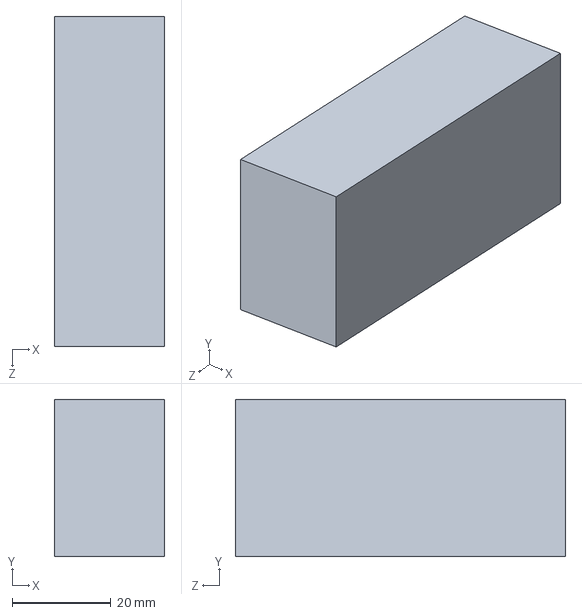
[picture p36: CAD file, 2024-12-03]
5. CAD Files/PLA Assembly/BatteryHolder.SLDPRT
22.2 x 31.8 x 66.7 mm

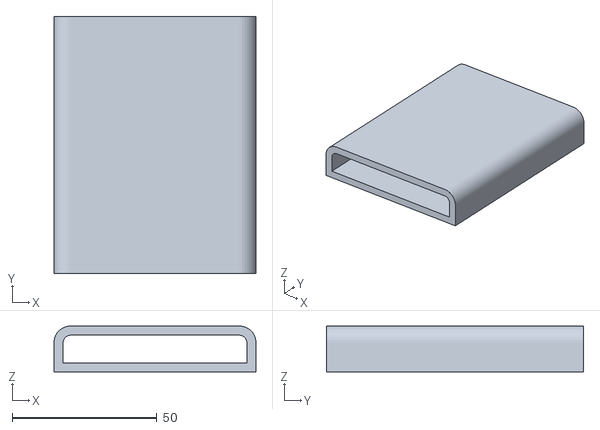
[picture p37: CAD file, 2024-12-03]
5. CAD Files/PLA Assembly/Print These PLA Parts/wirechannel stl.STL
69.8 x 88.9 x 15.9

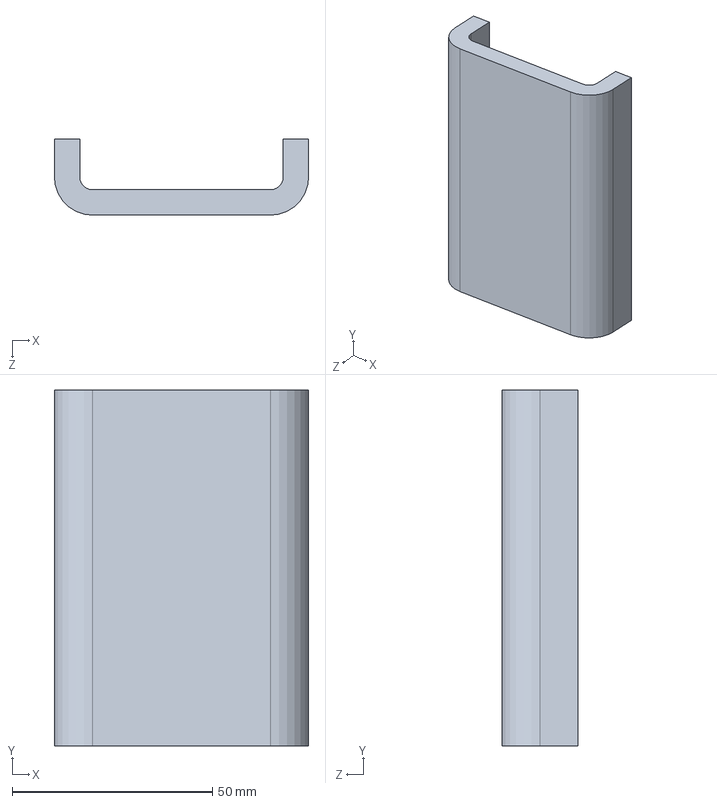
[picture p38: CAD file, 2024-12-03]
5. CAD Files/V3/V 3.2/wirechannel.SLDPRT
63.5 x 88.9 x 19.0 mm

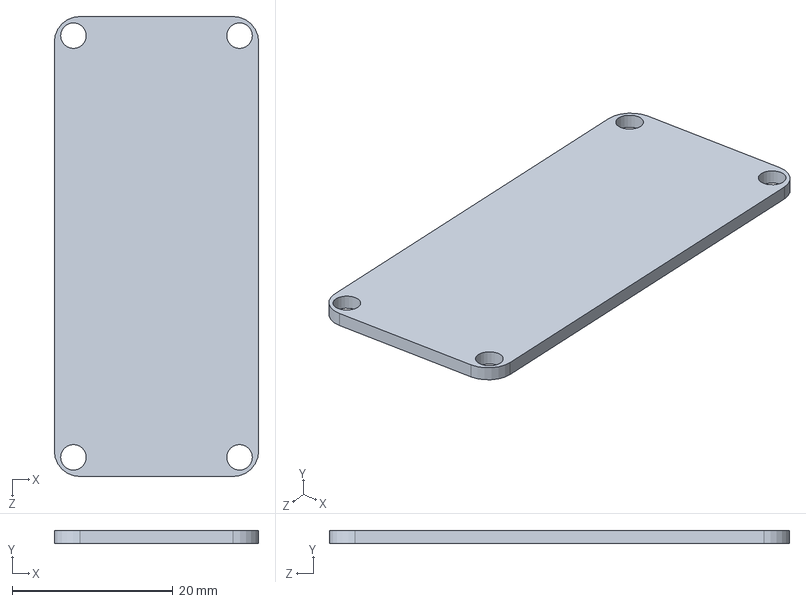
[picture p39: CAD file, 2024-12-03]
9. Testing Plans and Data (Drawings, Revision History File, Screening)/Drawings/PIN Pad + Door Closer Drawings/Microcontroller LoLin.SLDPRT
25.4 x 1.59 x 57.1 mm

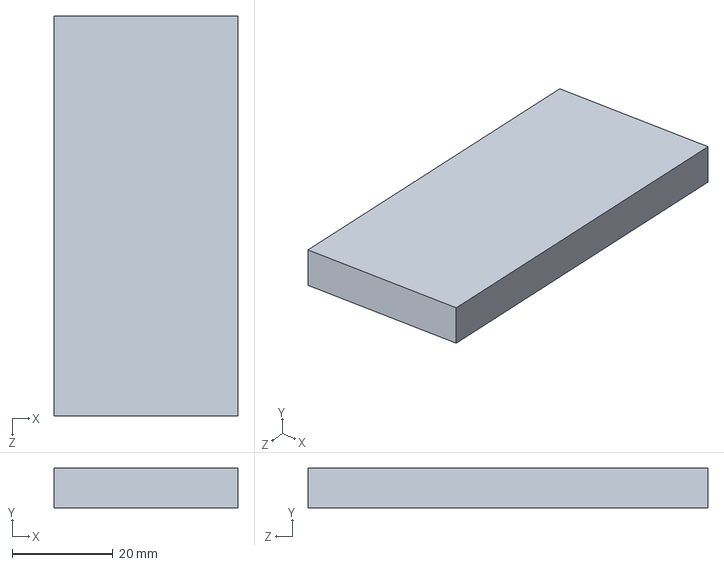
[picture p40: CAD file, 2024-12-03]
5. CAD Files/Circuitry Files/Basic Shapes/LCD.SLDPRT
36.5 x 7.94 x 79.4 mm

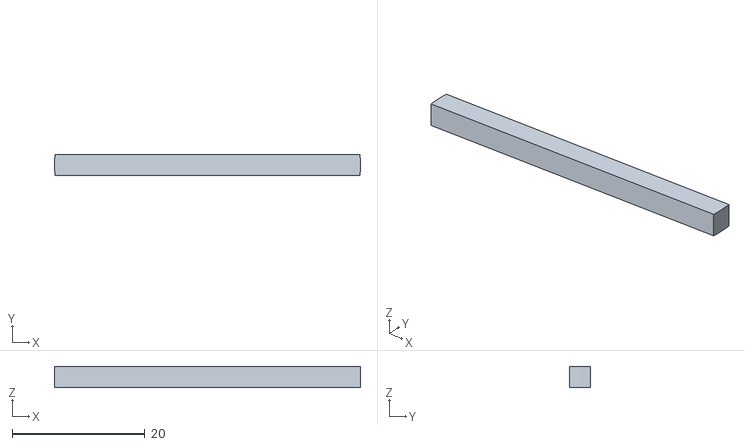
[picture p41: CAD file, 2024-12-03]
5. CAD Files/PLA Assembly/Print These PLA Parts/Speaker Support PLA stl.STL
46.0 x 3.17 x 3.17

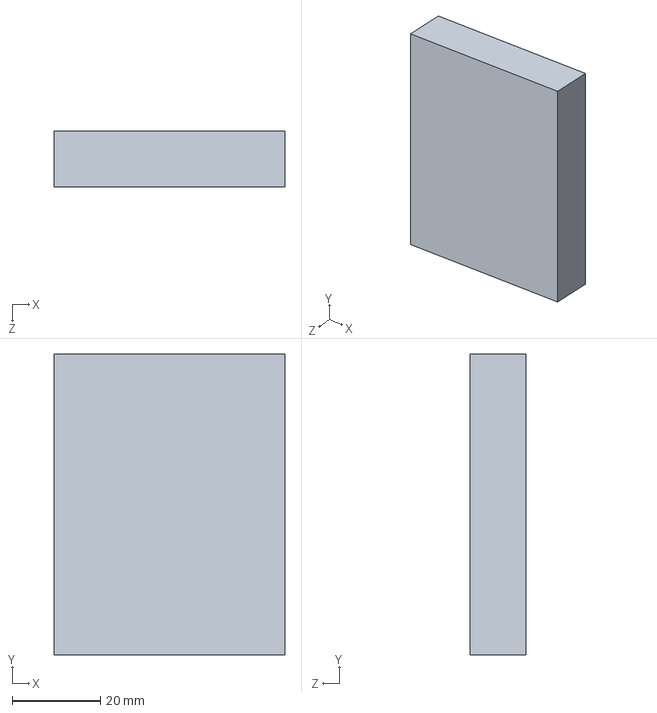
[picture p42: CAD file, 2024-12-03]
5. CAD Files/Circuitry Files/Basic Shapes/AdafruitMetro_ESP32-S3.SLDPRT
52.4 x 68.3 x 12.7 mm

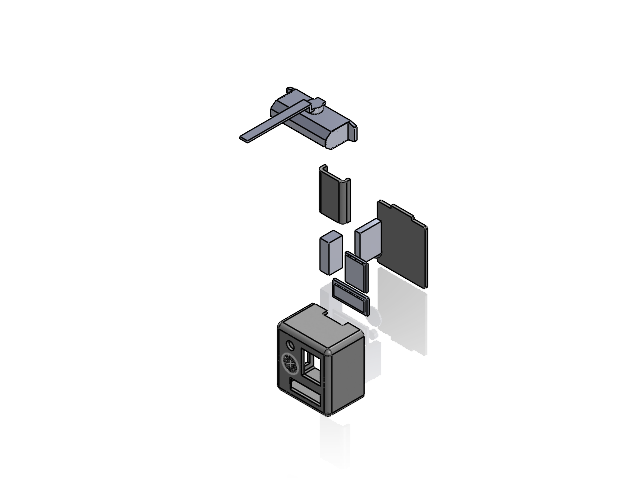
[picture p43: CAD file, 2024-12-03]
5. CAD Files/V3/V 3.2/Assembly V 3.2.SLDASM
Front Panel PLA
wirechannel
Back PLA
3x4Matrix
AdafruitMetro_ESP32-S3
BatteryHolder
LCD
LED_Indicator
speaker
Door Closer Real

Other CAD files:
5. CAD Files/Brayden_s CAD Work [Legacy Parts]/3x4 Matrix Support.SLDPRT
5. CAD Files/Brayden_s CAD Work [Legacy Parts]/Adafruit Metro Support.SLDPRT
5. CAD Files/Brayden_s CAD Work [Legacy Parts]/Assembly for PLA.SLDASM
5. CAD Files/Brayden_s CAD Work [Legacy Parts]/Back PLA.SLDPRT
5. CAD Files/Brayden_s CAD Work [Legacy Parts]/Battery Support.SLDPRT
5. CAD Files/Brayden_s CAD Work [Legacy Parts]/Final Assembly With Supports.SLDASM
5. CAD Files/Brayden_s CAD Work [Legacy Parts]/Front Side PLA Brayden.SLDPRT
5. CAD Files/Brayden_s CAD Work [Legacy Parts]/LCD Support.SLDPRT
5. CAD Files/Brayden_s CAD Work [Legacy Parts]/LED Indicator Support.SLDPRT
5. CAD Files/Brayden_s CAD Work [Legacy Parts]/Right Panel.SLDPRT
5. CAD Files/Brayden_s CAD Work [Legacy Parts]/Speaker Support.SLDPRT
5. CAD Files/Brayden_s CAD Work [Legacy Parts]/Support.SLDPRT
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

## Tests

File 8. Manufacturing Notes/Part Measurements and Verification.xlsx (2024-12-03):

Component | Width (in) | Length (in) | Height (in) | Radius (in) | Length of Wire | Activate? | Other Info | basic shape
Adafruit Metro - Circuit Python | 2.6875 in | 2.0625 in | 0.5 in | N/A | N/A |  |  | x
Standard LCD | 3.125 in | 1.4375 in | 0.3125 in | N/A | N/A |  |  | x
9V Battery Holder | 2.625 in | 0.875 in | 1.25 in | N/A | 7.5 in |  |  | x
Speaker | N/A | N/A | 0.125 in | 0.78125 in | 3.875 in |  |  | x
Red/Green LED Indicator | N/A | N/A | 0.375 in | 0.34375 in | N/A |  |  | x
3x4 Matrix Keypad | 2.6875 in | 2 in | 0.3125 in | N/A | N/A |  |  | x
10K Potentiometer (Breadboard Friendly) | N/A | 1 in | 1 in | 0.3125 in | N/A |  | Drowel and Nut included | na
10K Ohm (5%) Resisitors | N/A | N/A | N/A | N/A | 2.375 in |  |  | na
Micro Servo | 0.875 in | 0.4375 in | 1.375 in | N/A | 10.625 in |  | 3 Propellers and 3 Screws included | x
Adafruit Metro ESP32-S3 | 2.6875 in | 2.0625 in | 0.5 in | N/A | N/A

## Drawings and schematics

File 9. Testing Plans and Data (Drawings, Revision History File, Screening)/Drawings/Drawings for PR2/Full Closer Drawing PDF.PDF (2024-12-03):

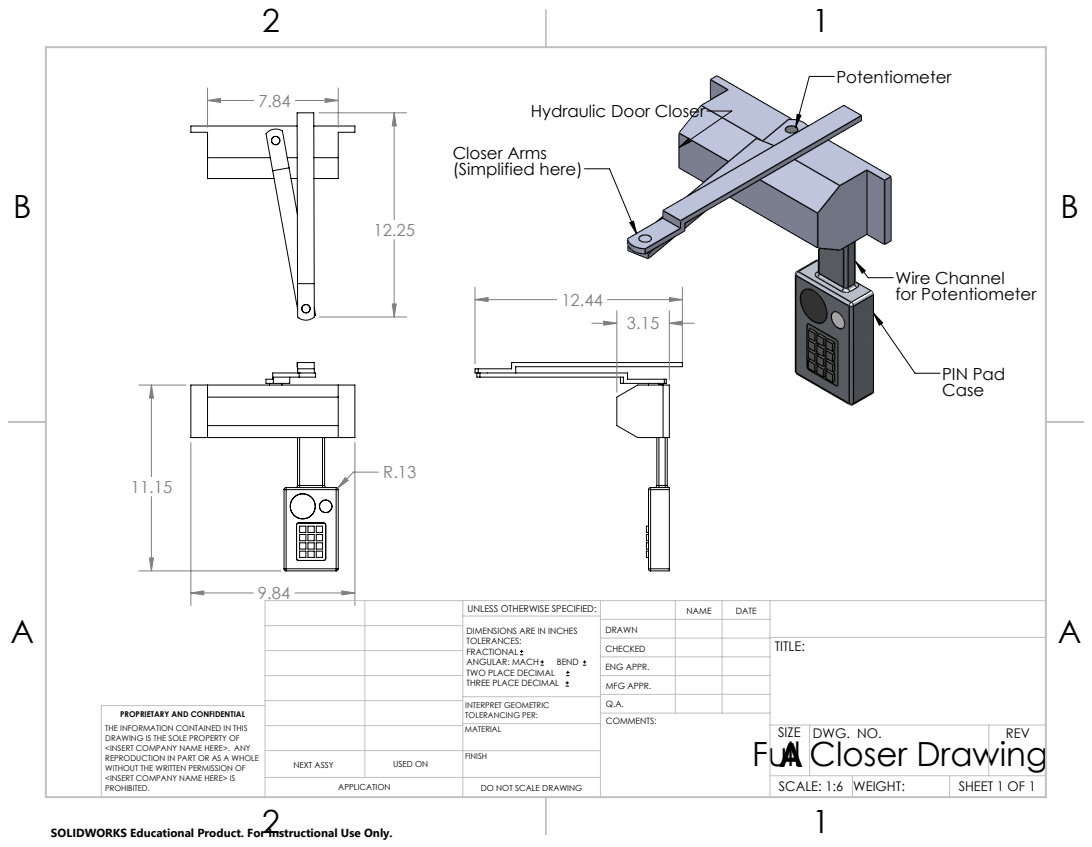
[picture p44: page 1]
PIN Pad; Wire Channel for Potentiometer; Closer Arms (Simplified here)

Hydraulic Door Closer

UNLESS OTHERWISE SPECIFIED: | | NAME | DATE
DIMENSIONS ARE IN INCHES TOLERANCES: FRACTIONAL ANGULAR: MACH BEND TWO PLACE DECIMAL THREE PLACE DECIMAL | DRAWN

CHECKED | | | TITLE:

ENG APPR.
MFG APPR.

INTERPRET GEOMETRIC TOLERANCING PER: | Q.A.
MATERIAL | Full Closer Drawing | SIZE A | DWG. NO. | REV

PROPRIETARY AND CONFIDENTIAL
THE INFORMATION CONTAINED IN THIS
DRAWING IS THE SOLE PROPERTY OF
<INSERT COMPANY NAME HERE>. ANY
REPRODUCTION IN PART OR AS A WHOLE
WITHOUT THE WRITTEN PERMISSION OF
<INSERT COMPANY NAME HERE> IS
PROHIBITED.

NEXT ASSY | USED ON | FINISH

APPLICATION | DO NOT SCALE DRAWING | | SCALE: 1:6 | WEIGHT: | SHEET 1 OF 1

SOLIDWORKS Educational Product. For Instructional Use Only.

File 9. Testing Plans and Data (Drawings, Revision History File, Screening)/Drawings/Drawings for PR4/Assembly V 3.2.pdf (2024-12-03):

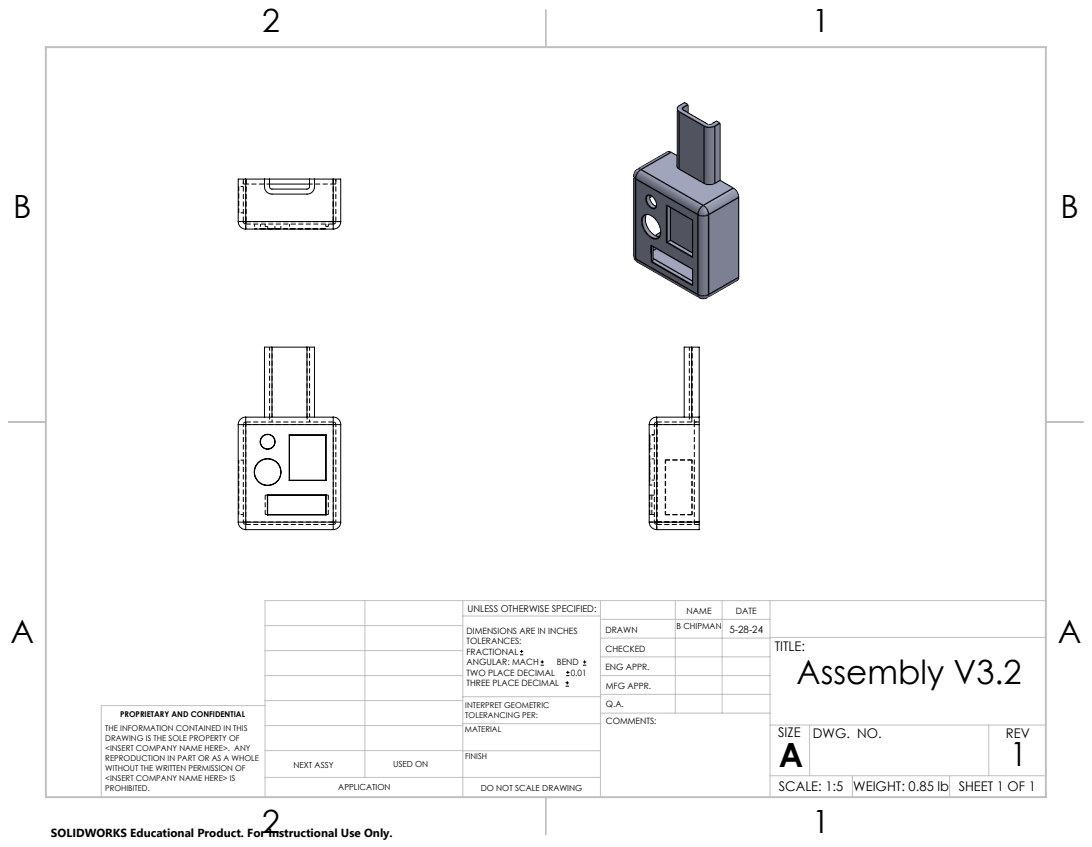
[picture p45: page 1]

UNLESS OTHERWISE SPECIFIED: | | NAME | DATE
DIMENSIONS ARE IN INCHES TOLERANCES: FRACTIONAL ANGULAR: MACH BEND TWO PLACE DECIMAL 0.01 THREE PLACE DECIMAL | DRAWN | | 5-28-24 B CHIPMAN

CHECKED | | | TITLE: Assembly V3.2

ENG APPR.
MFG APPR.

INTERPRET GEOMETRIC TOLERANCING PER: | Q.A.
MATERIAL | | SIZE A | DWG. NO. | REV 1

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

NEXT ASSY | USED ON | FINISH

APPLICATION | DO NOT SCALE DRAWING | | SCALE: 1:5 | WEIGHT: 0.85 lb | SHEET 1 OF 1

SOLIDWORKS Educational Product. For Instructional Use Only.

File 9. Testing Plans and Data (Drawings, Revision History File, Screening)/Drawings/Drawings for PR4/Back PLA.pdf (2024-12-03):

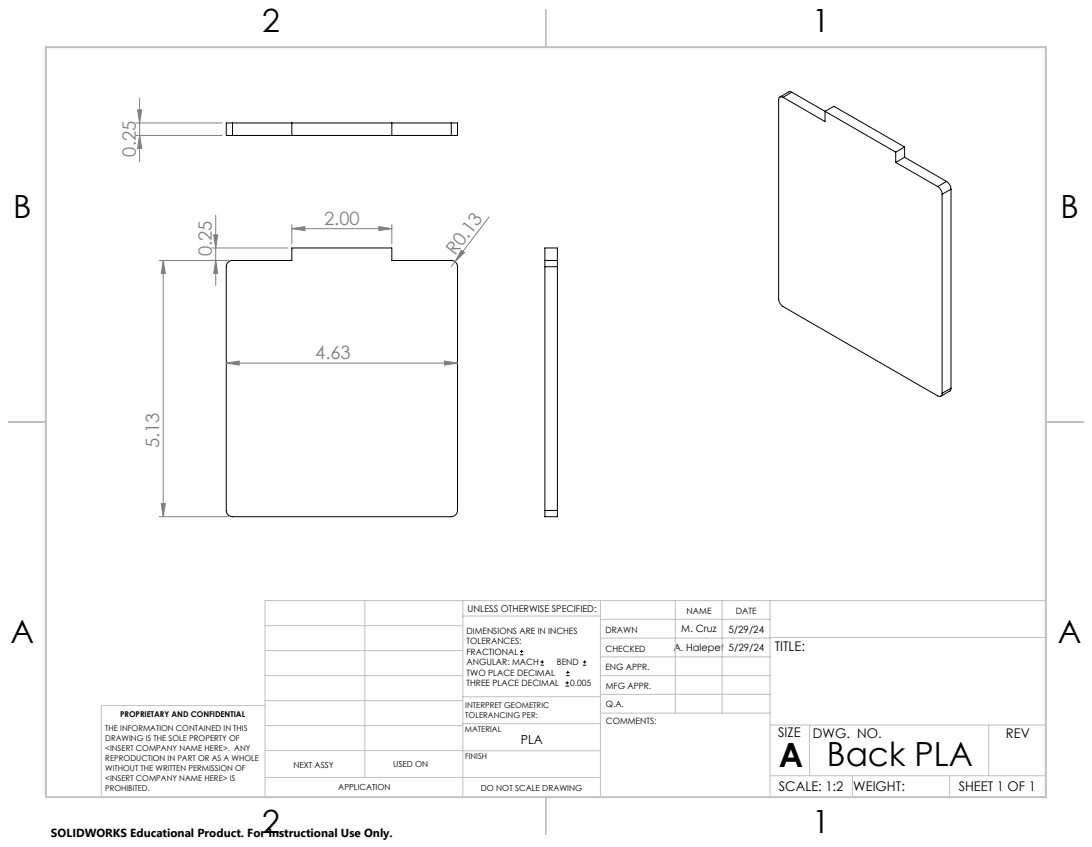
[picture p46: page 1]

UNLESS OTHERWISE SPECIFIED: | | NAME | DATE
DIMENSIONS ARE IN INCHES TOLERANCES: FRACTIONAL ANGULAR: MACH BEND TWO PLACE DECIMAL THREE PLACE DECIMAL 0.005 | DRAWN | M. Cruz | 5/29/24

CHECKED | A. Halepet 5/29/24 | | TITLE:

ENG APPR.
MFG APPR.

INTERPRET GEOMETRIC TOLERANCING PER: | Q.A.
MATERIAL PLA | | SIZE A | DWG. NO. Back PLA | REV

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

NEXT ASSY | USED ON | FINISH

APPLICATION | DO NOT SCALE DRAWING | | SCALE: 1:2 | WEIGHT: | SHEET 1 OF 1

SOLIDWORKS Educational Product. For Instructional Use Only.

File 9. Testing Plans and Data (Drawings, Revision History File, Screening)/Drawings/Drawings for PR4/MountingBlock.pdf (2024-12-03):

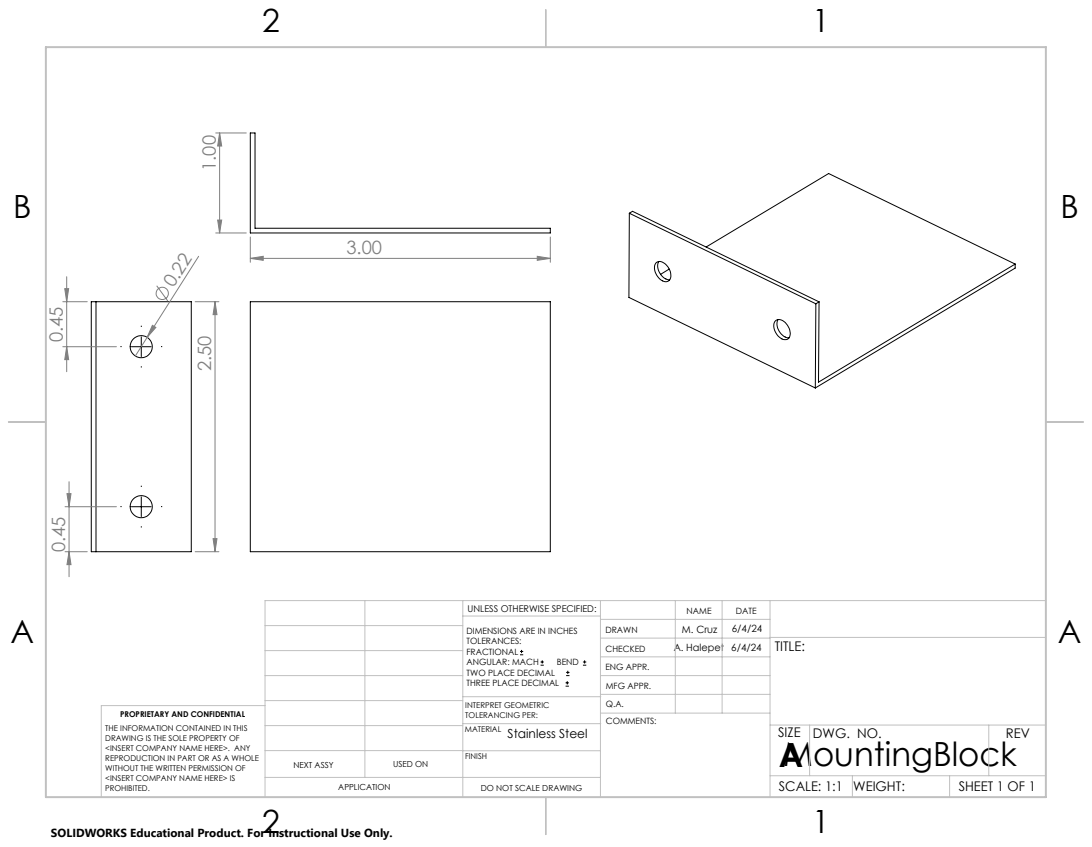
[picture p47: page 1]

UNLESS OTHERWISE SPECIFIED: | | NAME | DATE
DIMENSIONS ARE IN INCHES TOLERANCES: FRACTIONAL ANGULAR: MACH BEND TWO PLACE DECIMAL THREE PLACE DECIMAL | DRAWN | M. Cruz | 6/4/24

CHECKED | A. Halepet 6/4/24 | | TITLE:

ENG APPR.
MFG APPR.

INTERPRET GEOMETRIC TOLERANCING PER: | Q.A.
MATERIAL Stainless Steel | | SIZE A MountingBlock | DWG. NO. | REV

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

NEXT ASSY | USED ON | FINISH

APPLICATION | DO NOT SCALE DRAWING | | SCALE: 1:1 | WEIGHT: | SHEET 1 OF 1

SOLIDWORKS Educational Product. For Instructional Use Only.

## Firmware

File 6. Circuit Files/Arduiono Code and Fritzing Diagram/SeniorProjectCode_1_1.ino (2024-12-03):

// Limit Switch
#define LIMIT_SWITCH_PIN 0

// Keypad
#include <Keypad.h>
const byte ROWS = 4; 
const byte COLS = 3; 
char hexaKeys[ROWS][COLS] = {
  {'1', '2', '3'},
  {'4', '5', '6'},
  {'7', '8', '9'},
  {'*', '0', '#'}
};
byte rowPins[ROWS] = {45, 47, 49, 51}; 
byte colPins[COLS] = {39, 41, 43}; 
Keypad customKeypad = Keypad(makeKeymap(hexaKeys), rowPins, colPins, ROWS, COLS); 

// LCD
#include <LiquidCrystal.h>
const int rs = 13, en = 12, d4 = 11, d5 = 10, d6 = 9, d7 = 8;
LiquidCrystal lcd(rs, en, d4, d5, d6, d7);

// LED Red and Green
#define GREEN 6
#define RED 5

// Servo
#include <Servo.h>
Servo myservo;  // create servo object to control a servo

// Limit Switch
int limitSwitch = 7;

// Buzzer
#define BUZZER 2

// Passcode
#define Password_Length 8 
char Data[Password_Length]; 
char Master[Password_Length] = "1234567"; 
char Last_Passcode[Password_Length] = "";  // Store last used passcode
char User1[Password_Length] = "7654321";  // Additional user passcode
char User2[Password_Length] = "1122334";  // Additional user passcode
byte data_count = 0;
bool Pass_is_good;
char customKey;
bool Status = 1;
char lastUser = ' '; // Track who used the pinpad last

// Change passcode
bool changePasscodeMode = false;
char tempPasscode1[Password_Length];
char tempPasscode2[Password_Length];
byte temp_count = 0;

unsigned long previousMillis = 0;
const long interval = 120000; // 2 minutes in milliseconds

void setup() {
  // Setup code
  pinMode(GREEN, OUTPUT);
  pinMode(RED, OUTPUT);
  digitalWrite(RED, LOW);
  digitalWrite(GREEN, HIGH);
  pinMode(BUZZER, OUTPUT);
  noTone(BUZZER);
  myservo.attach(3); 
  myservo.write(0);

  Serial.begin(9600);
  pinMode(LIMIT_SWITCH_PIN, INPUT);
  lcd.begin(16, 2);
  lcd.print("Monitoring...");
  pinMode(limitSwitch, INPUT_PULLUP);
}

void loop() {
  // Main code
  unsigned long currentMillis = millis();

  // Check if limit switch is open
  if (digitalRead(limitSwitch) == 1) { // Assuming 1 means open
    if (currentMillis - previousMillis >= interval) {
      previousMillis = currentMillis;

      while (digitalRead(limitSwitch) == 1) { // Alarm logic
        lcd.setCursor(0, 0); // Set cursor to top-left before printing
        lcd.print("Alert!");
        tone(BUZZER, 1000);
        digitalWrite(RED, HIGH);
        digitalWrite(GREEN, LOW);
        delay(200); // Brief delay for user to see the alert
        lcd.clear(); // Clear the alert message
        noTone(BUZZER);
        digitalWrite(RED, LOW);
        delay(200);
      }
    }
  } else {
    previousMillis = currentMillis; // Reset the timer if limit switch is closed
    noTone(BUZZER);
    digitalWrite(RED, LOW);
    digitalWrite(GREEN, HIGH);
    lcd.setCursor(0, 0); // Set cursor to top-left before printing
    lcd.print("Monitoring..."); // Reprint monitoring message
  }

  customKey = customKeypad.getKey();
  if (customKey) {
    if (changePasscodeMode) {
      handleChangePasscode(customKey);
    } else {
      handleRegularMode(customKey);
    }
  }

  if (data_count == Password_Length - 1) {
    lcd.clear();
    if (!strcmp(Data, Master)) {
      handleCorrectPasscode('M');
    } else if (!strcmp(Data, User1)) {
      handleCorrectPasscode('U');
    } else if (!strcmp(Data, User2)) {
      handleCorrectPasscode('V');
    } else {
      handleIncorrectPasscode();
    }
    clearData();  
  }
}

void handleRegularMode(char key) {
  if (key == '*') {
    if (data_count == 0) {
      changePasscodeMode = true;
      lcd.clear();
      lcd.print("Change Passcode");
      delay(1000);
      lcd.clear();
      lcd.print("Enter Current");

    } else {
      Data[data_count] = key;
      lcd.setCursor(data_count, 1);
      lcd.print(Data[data_count]);
      data_count++;
    }
  } else if (key == '#') {
    displayLastUser();
  } else {
    Data[data_count] = key;
    lcd.setCursor(data_count, 1);
    lcd.print(Data[data_count]);
    data_count++;
  }
}

void handleChangePasscode(char key) {
  if (temp_count == 0) {
    lcd.clear();
    lcd.print("Enter New");
    lcd.setCursor(0, 1);
  }
  tempPasscode1[temp_count] = key;
  lcd.print(tempPasscode1[temp_count]);
  temp_count++;

  if (temp_count == Password_Length - 1) {
    lcd.clear();
    lcd.print("Confirm New");
    lcd.setCursor(0, 1);
    temp_count = 0;
    while (temp_count < Password_Length - 1) {
      customKey = customKeypad.getKey();
      if (customKey) {
        tempPasscode2[temp_count] = customKey;
        lcd.print(tempPasscode2[temp_count]);
        temp_count++;
      }
    }

    if (!strcmp(tempPasscode1, tempPasscode2)) {
      strcpy(User1, tempPasscode1);
      lcd.clear();
      lcd.print("Passcode Updated");
      delay(1000);
      lcd.clear();
      lcd.print("Monitoring...");
    } else {
      lcd.clear();
      lcd.print("Mismatch");
      delay(1000);
      lcd.clear();
      lcd.print("Monitoring...");
    }

    clearTempData();
    changePasscodeMode = false;
  }
}

void handleCorrectPasscode(char user) {
  lcd.print("Correct");
  storeLastPasscode(Data);
  lastUser = user;
  delay(5000);
  if (Status == 1) {
    myservo.write(90);
    Status = 0;
  } else if (Status == 0) {
    myservo.write(0);
    Status = 1;
  }
}

void handleIncorrectPasscode() {
  lcd.print("Incorrect");
  tone(BUZZER, 1000);
  delay(500);
  noTone(BUZZER);
  delay(500);
  lcd.clear();
  lcd.print("Monitoring");
}

void storeLastPasscode(char *passcode) {
  strcpy(Last_Passcode, passcode);
}

void clearData() {
  while (data_count != 0) {
    Data[data_count--] = 0;
  }
}

void clearTempData() {
  for (int i = 0; i < Password_Length; i++) {
    tempPasscode1[i] = 0;
    tempPasscode2[i] = 0;
  }
  temp_count = 0;
}

void displayLastUser() {
  lcd.clear();
  lcd.print("Last User: ");
  if (lastUser == 'M') {
    lcd.print("Master");
  } else if (lastUser == 'U') {
    lcd.print("User1");
  } else if (lastUser == 'V') {
    lcd.print("User2");
  } else {
    lcd.print("None");
  }
  delay(2000);
  lcd.clear();
  lcd.print("Monitoring...");
}
